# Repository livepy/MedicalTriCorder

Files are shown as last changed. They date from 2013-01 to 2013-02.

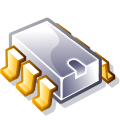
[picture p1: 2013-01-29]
Python/Emulator/ic.png

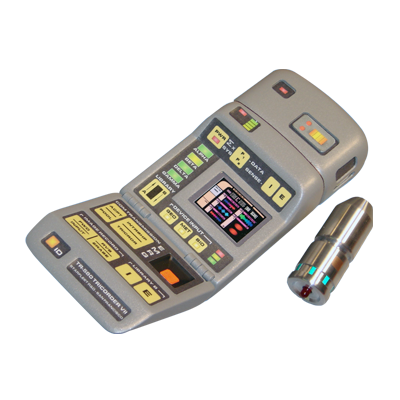
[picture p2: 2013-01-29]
Python/tricorder.png

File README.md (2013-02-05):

Medical TriCorder
================

The Medical TriCorder is written in Python and interfaces with an arduino powered Hand Scanner Unit (HSU). The software for the Medical TriCorder is designed to run on Windows, Linux, Mac OS X, and the Raspberry Pi.

Please keep in mind all code and schematics are PRE-ALPHA.

The goal of the Medical TriCorder is to create a fast, efficent, and open source way to quickly get the core vitals of a patient.

The HSU is the main device of this project and will gather Beats Per Minute, SpO2, and Tempature of a patient and transmit it back to the TriCorder application for easy readout.

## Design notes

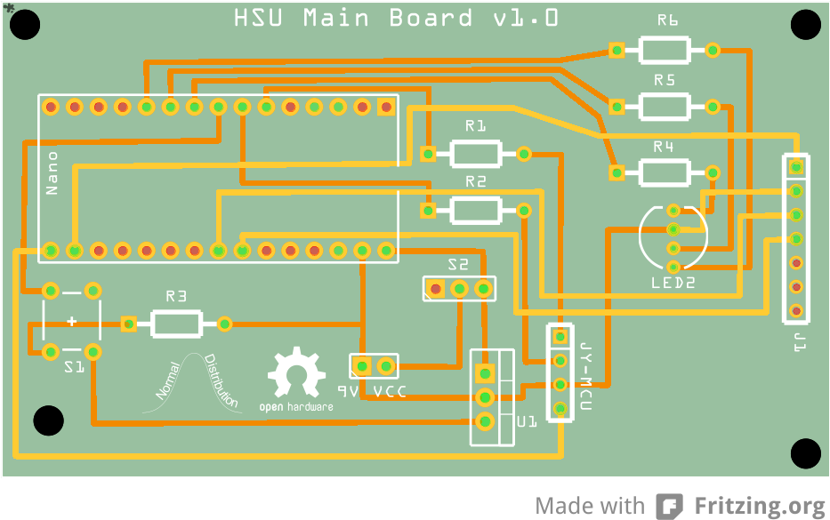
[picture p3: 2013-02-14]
HSU/Schematic/MainBoard/PCB.png

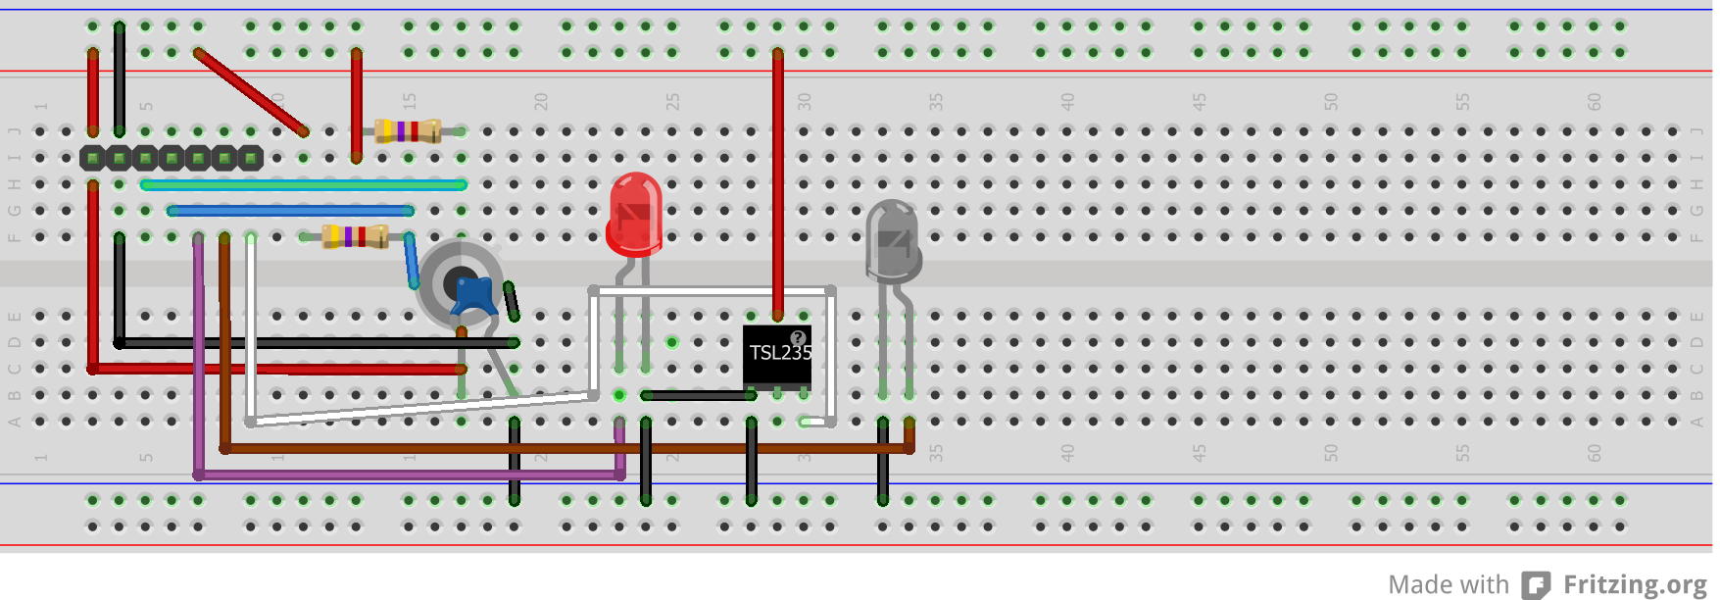
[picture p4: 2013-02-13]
HSU/Schematic/SensorBoard/BreadboardLayout.png

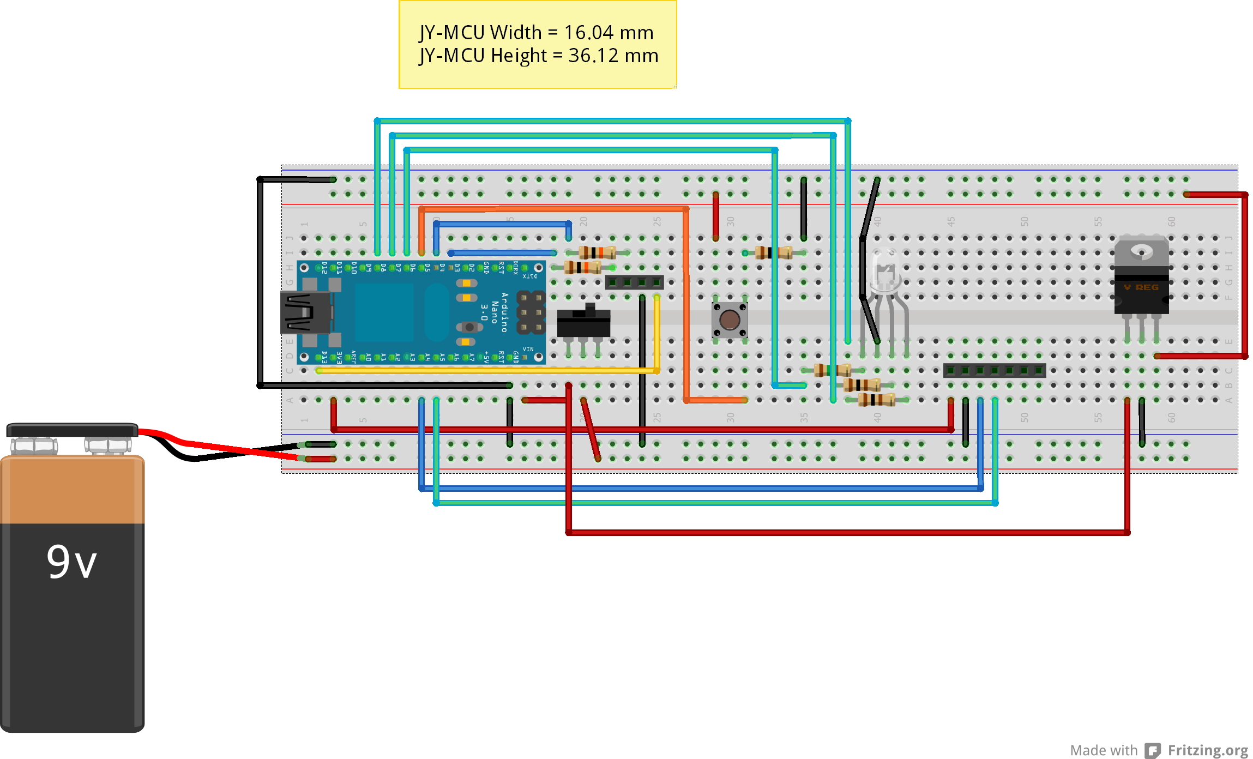
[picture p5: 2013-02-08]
HSU/Schematic/MainBoard/BreadboardLayout.png

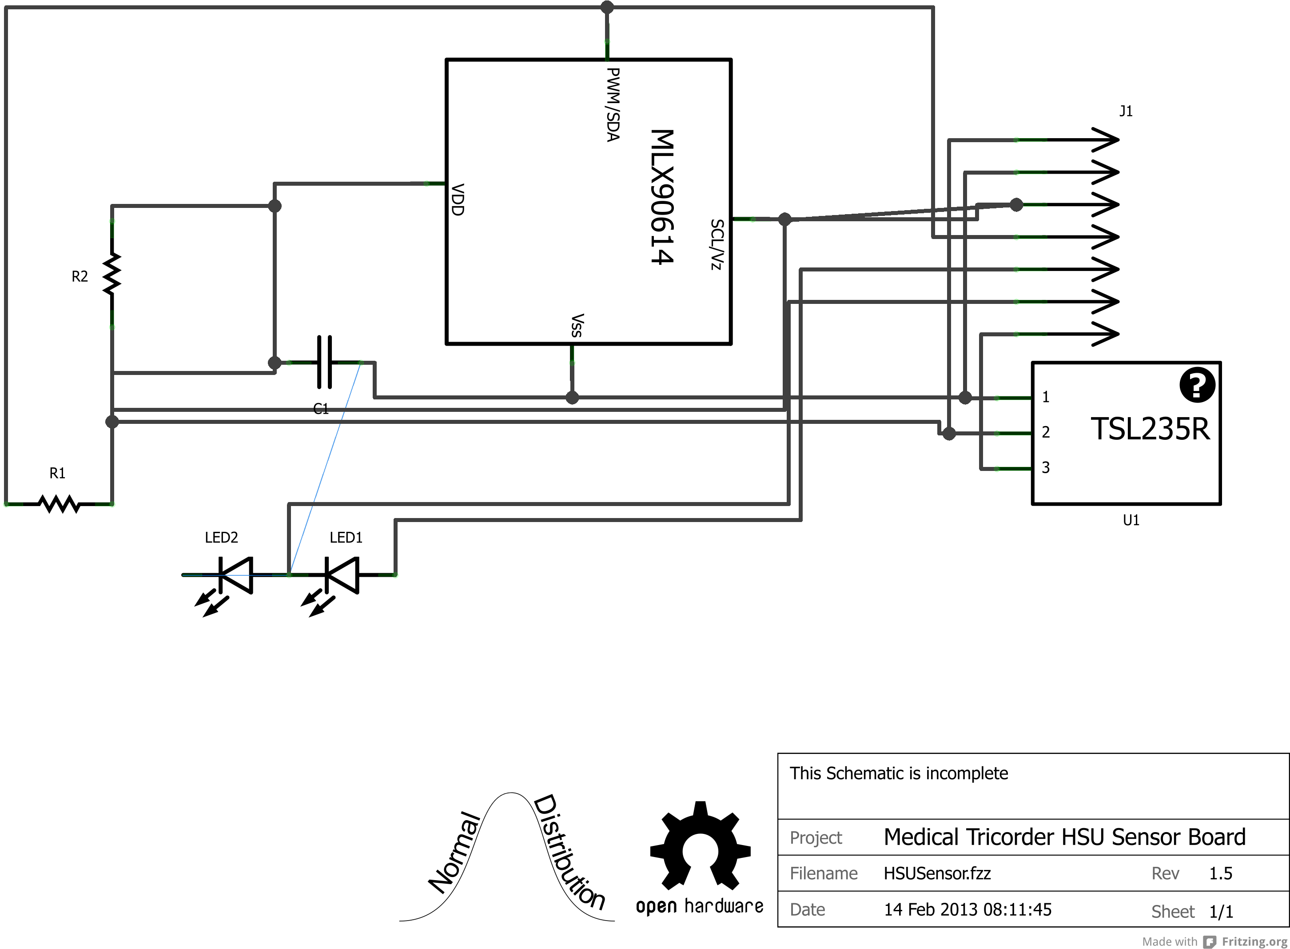
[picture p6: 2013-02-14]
HSU/Schematic/SensorBoard/Schematic.png

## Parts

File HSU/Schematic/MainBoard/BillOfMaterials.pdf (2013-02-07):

# Bill of Materials: HSU Main Board

Wednesday, February 6 2013

## Assembly List

Label | Part Type | Properties
9V
VCC | Battery block 9V | voltage 9V
J1 | Generic female header -
| 7 pins | package THT; gender ♀; hole shape Square; pins 7; pin
| | spacing 0.1in (2.54mm)
JY- MCU | Generic female header -
| 4 pins | package THT; gender ♀; hole shape Square; pins 4; pin
| | spacing 0.1in (2.54mm)
LED2 | RGB LED (com.
| cathode, rgb) | package 5 mm [THT]; pin order rgb; polarity common
| | cathode; rgb RGB
Nano | Arduino Nano v3.0 | processor ATmega; variant Arduino Nano v3.0
R1 | 10k Ω Resistor | package THT; resistance 10kΩ; rated power 0.25 watt;
| | footprint 400 mil
R2 | 10k Ω Resistor | package THT; resistance 10kΩ; rated power 0.25 watt;
| | footprint 400 mil
R3 | 10k Ω Resistor | package THT; resistance 10kΩ; rated power 0.25 watt;
| | footprint 400 mil
R4 | 150 Ω Resistor | package THT; resistance 150Ω; rated power 0.25 watt;
| | footprint 400 mil
R5 | 100 Ω Resistor | package THT; resistance 100Ω; rated power 0.25 watt;
| | footprint 400 mil
R6 | 100 Ω Resistor | package THT; resistance 100Ω; rated power 0.25 watt;
| | footprint 400 mil
S1 | Pushbutton | package [THT]
S2 | Toggle Switch | package THT; switching circuit SPDT
U1 | Voltage Regulator - 5V | package TO220 [THT]; voltage 5V

## Shopping List

Amount | Part Type | Properties
1 RGB LED (com.
| cathode, rgb) | package 5 mm [THT]; pin order rgb; polarity common
| | cathode; rgb RGB

### 1 Generic female header -

| 4 pins | package THT; gender ♀; hole shape Square; pins 4; pin
| | spacing 0.1in (2.54mm)

### 1 Generic female header - package THT; gender ♀; hole shape Square; pins 7; pin

Amount | Part Type | Properties
| 7 pins | spacing 0.1in (2.54mm)
2 | 100 Ω Resistor | package THT; resistance 100Ω; rated power 0.25 watt; footprint 400 mil
3 | 10k Ω Resistor | package THT; resistance 10kΩ; rated power 0.25 watt; footprint 400 mil
1 | 150 Ω Resistor | package THT; resistance 150Ω; rated power 0.25 watt; footprint 400 mil
1 | Toggle Switch | package THT; switching circuit SPDT
1 | Voltage Regulator - 5V | package TO220 [THT]; voltage 5V
1 | Pushbutton | package [THT]
1 | Arduino Nano v3.0 | processor ATmega; variant Arduino Nano v3.0
1 | Battery block 9V | voltage 9V

Exported with Fritzing 0.7.10- http://fritzing.org

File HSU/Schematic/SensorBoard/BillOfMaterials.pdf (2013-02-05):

# Bill of Materials: HSU Sensor Board

### Tuesday, February 5 2013

## Assembly List

Label | Part Type | Properties
C1 | Ceramic Capacitor | package 100 mil [THT, multilayer]; capacitance 0.1µF; voltage 6.3V
J1 | Generic male header - 7

### pins

| | package THT; gender ♂; pins 7; pin spacing 0.1in (2.54mm)
MLX90614 | MLX90614 Infrared

### Thermometer

R1 | 4.7k Ω Resistor | package THT; tolerance ±5%; bands 4; resistance 4.7kΩ; pin spacing 400 mil
R2 | 4.7k Ω Resistor | package THT; tolerance ±5%; bands 4; resistance 4.7kΩ; pin spacing 400 mil

## Shopping List

Amount | Part Type | Properties

### 1 MLX90614 Infrared Thermometer

1 | Ceramic Capacitor | package 100 mil [THT, multilayer]; capacitance 0.1µF; voltage 6.3V
1 | Generic male header - 7 pins | package THT; gender ♂; pins 7; pin spacing 0.1in (2.54mm)
2 | 4.7k Ω Resistor | package THT; tolerance ±5%; bands 4; resistance 4.7kΩ; pin spacing 400 mil

### Exported with Fritzing 0.7.10- http://fritzing.org

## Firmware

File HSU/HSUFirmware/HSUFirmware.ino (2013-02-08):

#include <EEPROM.h>
#include <i2cmaster.h>
#include <SoftwareSerial.h>

SoftwareSerial btConnection = SoftwareSerial(3, 4);
boolean bUseLocalSerial = false;
int scanButton = 5;
int btPowerPIN = 13;
int redRGBLEDPIN = 6;
int greenRGBLEDPIN = 7;
int blueRGBLEDPIN = 8;

void setup()
{
  Serial.begin(38400);
  
  if (EEPROM.read(0) == 1)
  {
    bUseLocalSerial = false;
  }
  else if (EEPROM.read(0) == 0)
  {
    bUseLocalSerial = true;
  }
  
  pinMode(btPowerPIN, OUTPUT);
  pinMode(scanButton, INPUT);
  
  if (bUseLocalSerial)
  {
    Serial.println("RDY BT OFF");
    analogWrite(btPowerPIN, 0);
  }
  else
  {
    Serial.println("RDY BT ON");
    analogWrite(btPowerPIN, 255);
    btConnection.begin(38400);
    btConnection.println("RDY BT ON");
  }
  
  i2c_init(); //Initialise the i2c bus for temp readings
  PORTC = (1 << PORTC4) | (1 << PORTC5);//enable pullups
  
  setRGBColor(0, 255, 0);
}

void loop()
{
  byte bCommand;
  
  if (digitalRead(scanButton))
  {
    if (bUseLocalSerial)
    {
      Serial.println("SCN");
      getSensorData();
    }
    else
    {
      btConnection.println("SCN");
      getSensorData();
    }
  }
  
  if (btConnection.available())
  {
    bCommand = btConnection.read();

    switch (bCommand)
    {
      case 0xA1:
        //Ident Command
        btConnection.println("Medical TriCorder HSU v1.0");
        break;
      case 0xA2:
        //Change PIN Command
        break;
      default:
        break;
    }
  }
}

void getSensorData()
{
  setRGBColor(0, 0, 255);
  delay(1500);
  char buffer[10];
  //THIS IS SIMULATED
  int iBPM = random(72, 85);
  //THIS IS SIMULATED
  int SpO2 = random(90, 100);
  String Temp;
  String sReturn;
  
  Temp = dtostrf(getTemp(false), 5, 2, buffer);
  
  sReturn = "ACK," + (String)iBPM + "," + (String)SpO2 + "," + Temp;
  
  if (bUseLocalSerial)
  {
    Serial.println(sReturn);
  }
  else
  {
    btConnection.println(sReturn);
  }
  
  setRGBColor(0, 255, 0);
}

float getTemp(boolean bReturnCelcius)
{
    int dev = 0x5A<<1;
    int data_low = 0;
    int data_high = 0;
    int pec = 0;
    
    i2c_start_wait(dev+I2C_WRITE);
    i2c_write(0x07);
    
    // read
    i2c_rep_start(dev+I2C_READ);
    data_low = i2c_readAck(); //Read 1 byte and then send ack
    data_high = i2c_readAck(); //Read 1 byte and then send ack
    pec = i2c_readNak();
    i2c_stop();
    
    //This converts high and low bytes together and processes temperature, MSB is a error bit and is ignored for temps
    double tempFactor = 0.02; // 0.02 degrees per LSB (measurement resolution of the MLX90614)
    double tempData = 0x0000; // zero out the data
    int frac; // data past the decimal point
    
    // This masks off the error bit of the high byte, then moves it left 8 bits and adds the low byte.
    tempData = (double)(((data_high & 0x007F) << 8) + data_low);
    tempData = (tempData * tempFactor)-0.01;
    
    float celcius = tempData - 273.15;
    float fahrenheit = (celcius*1.8) + 32;
    
    if (bReturnCelcius)
    {
      return celcius;
    }
    else
    {
      return fahrenheit;
    }
}

void setRGBColor(int iRed, int iGreen, int iBlue)
{
  analogWrite(redRGBLEDPIN, iRed);
  analogWrite(greenRGBLEDPIN, iGreen);
  analogWrite(blueRGBLEDPIN, iBlue);
}

void serialEvent()
{
  byte bCommand;
  
  if (Serial.available())
  {
    bCommand = Serial.read();
    
    switch (bCommand)
    {
      case 0xF0:
        //Return BT Status
        if (bUseLocalSerial)
        {
          Serial.println("BT OFF");
        }
        else
        {
          Serial.println("BT ON");
        }
        break;
      case 0xF1:
        //Turn BT On
        bUseLocalSerial = false;
        EEPROM.write(0, 1);
        analogWrite(btPowerPIN, 255);
        Serial.println("OK BT ON");
        btConnection.begin(38400);   
        break;
      case 0xF2:
        //Turn BT Off
        bUseLocalSerial = true;
        EEPROM.write(0, 0);
        analogWrite(btPowerPIN, 0);
        Serial.println("OK BT OFF");
        btConnection.end();
        break;          
      case 0xA1:
        //Ident Command
        Serial.println("Medical TriCorder HSU v1.0");
        break;
      case 0xA2:
        //Change PIN Command
        break;
      default:
        break;
    }
  }
}

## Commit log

2013-01-21 Added new label and arduino hand scanner sketch.
    Added Temp Label
    Added TC Hand Scanner Sketch
    Resized Form
    Changed Form Title
2013-01-22 Created the arduino code to read the pulse sensor.
2013-01-24 Fritzing Drawing Added
    Added fritzing drawing and exported the PCB and schematic layouts for
    easy online viewing. This schematic only contains the connections for
    the BlueTooth module and the VCC line.
    [TCHandScanner.fzz]
2013-01-25 Added code to connect to HSU
    Added arduino code for the command protocol. Also added sample data
    returns from the arduino. Python application now sends commands to the
    HSU.
2013-01-25 Added flag for local serial connection on the arduino
2013-01-25 Added three new command protocol bytes allowing the bluetooth module to be disabled.
    [TCHandScanner.fzz]
2013-01-25 Threading and Emulator Created
    Added threading to the main application to retrieve live data from the
    Created threading to enable the live display of the data from the HSU.
    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
2013-01-30 Class Modification
    Added class definitions to the main PDE files. This will enable the
    applications to be compiled.
    Added a check to the appIcon byte array to verify it isn't null before
    setting the frame icon.
2013-01-31 New Firmware and Schematics
    Updated firmware with the new HSU protocol.
    Added scan button press detection in the firmware.
    Updated schematics to include the scan button.
    Parts List is now a PDF and renamed to Bill Of Materials
    [TCHandScanner.fzz]
2013-02-01 Changed Name of TCHandScanner
    Changed the name of all references of TCHandScanner to HSU. Changed the
    PCB layout to reduce the size. Changed the default PCB grid spacing from
    0.1 in to 1 mm.
    [HSU.fzz, TCHandScanner.fzz]
2013-02-05 HSU Firmware Update (RGB LED)
    Added HSUFirmware folder for future libraries
    Changed BT power PIN to D5
    Added PINS for RGB LED (D6, D7, D8)
    Added setRGBColor method
    Added status colors
    [HSU.fzz]
2013-02-05 HSU PCB Update
    Resized the Main Board PCB
    Created the Sensor Board Fritzing Document
    Added a parts directory for Fritzing
    Added the MLX90614 Part
    Added the IR LED Part
    [HSU.fzz, HSUSensor.fzz]
2013-02-05 HSU Sensor Board Update
    MLX90614 added to board.
    [HSUSensor.fzz]
2013-02-06 Firmware Update
    Updated the firmware to support the MLX90614.
    [HSU.fzz]
2013-02-06 Schematic Update
    Updated HSU Main Board Schematic for connections to the Sensor Board for
    the MLX90614 sensor.
    [HSU.fzz, HSUSensor.fzz]
2013-02-06 Updated Main Board Schematics
    Updated the Main Board PCB to include a power switch (S2).
    [HSU.fzz]
2013-02-07 Schematic Update
    Added a 7805 to the Main Board. Noticed to much current being drawing by
    devices, added an independent voltage regulator to reduce the strain of
    current on the micro-controller.
    [HSU.fzz]
2013-02-07 Schematic Update
    Re-routed the 7805 (U1) VCC pin to the power switch (S2) so that the
    7805 will be off when power is off.
    [HSU.fzz]
2013-02-08 Schematic and Firmware Updated
    Rerouted JY-MCU (J1) VCC from D5 to D13.
    Updated Firmware to set full PWM duty cycle on D13 when BT is ON.
    [HSU.fzz]
2013-02-08 Schematic and Firmware Update
    Moved JY-MCU TX & RX pins to D3 & D4.
    Moved scan button (S1) to pin D5.
    Updated firmware to reflect new JY-MCU pins and scan button pin.
    [HSU.fzz]
2013-02-09 Sensor Board Schematic Update
    Added the TSL235R Fritzing Part
    Added the routes for the IR LED (LED2) and Red LED (LED 1)
    Added 3D rendering for the PCB
    [HSUSensor.fzz]
2013-02-11 Updated Schematics
    Moved the MLX90614 to be in line with LED2.
    Added 4 mounting holes (drill holes) to the main board.
    [HSU.fzz, HSUSensor.fzz]
2013-02-13 Schematic Update
    Changed the VCC input of the power switch (S2) of the main board.
    Removed the super flux LED and replaced it with a standard bright LED
    (LED2) on the sensor board.
    Removed the 3D rendering of the PCB until we get closer to ordering a
    prototype PCB.
    [HSU.fzz, HSUSensor.fzz]
2013-02-13 Schematic Update
    -Corrected an issue with the image exports-
    * Changed the VCC input of the power switch (S2) of the main board.
    * Removed the super flux LED and replaced it with a standard bright LED
    * Removed the 3D rendering of the PCB until we get closer to ordering a
    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
    [HSU.fzz]
2013-02-14 Schematic Updated
    * Added the Open Hardware Logo to all PCBs and Schematics
    * Added the Normal Distribution Logo to all PCBs and Schematics
    [HSU.fzz, HSUSensor.fzz]
